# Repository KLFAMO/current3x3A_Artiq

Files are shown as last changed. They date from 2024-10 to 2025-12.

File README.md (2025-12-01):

# current3x3A_Artiq
3 channel current driver (up to 3A each channel) compatible with Artiq

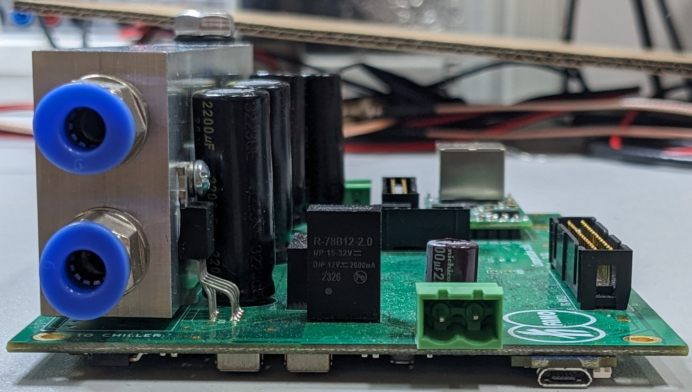
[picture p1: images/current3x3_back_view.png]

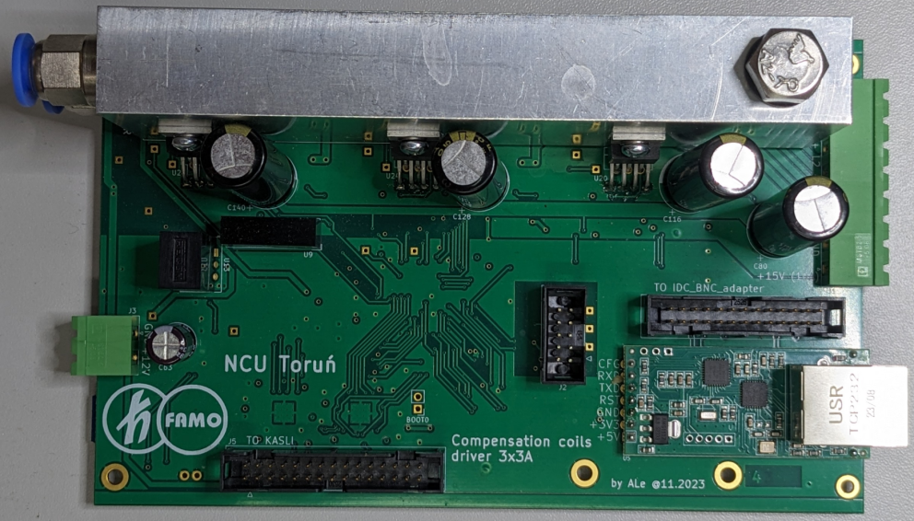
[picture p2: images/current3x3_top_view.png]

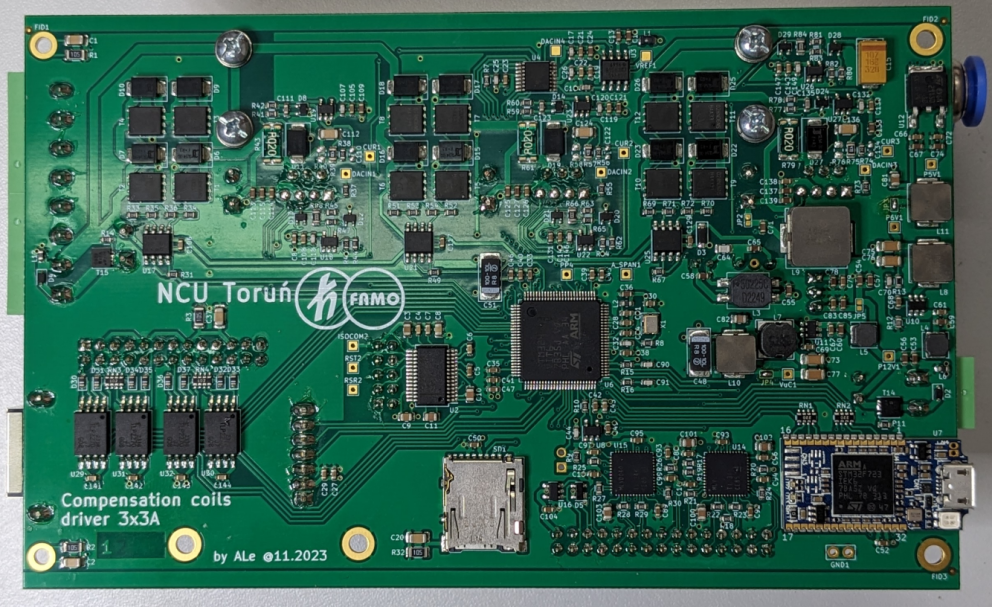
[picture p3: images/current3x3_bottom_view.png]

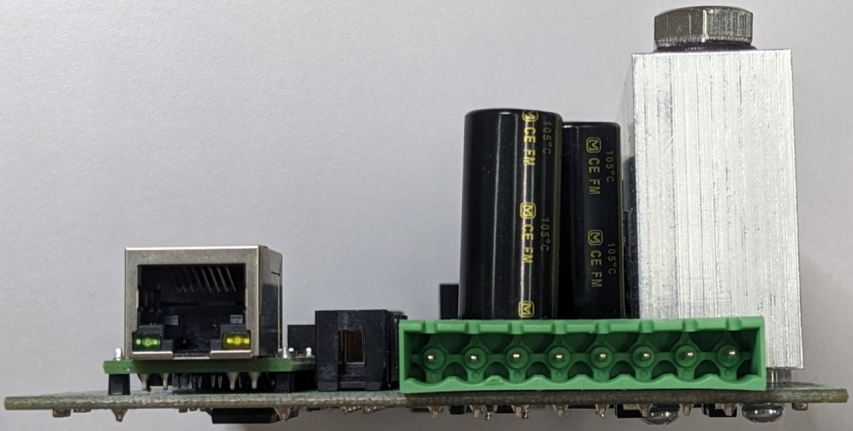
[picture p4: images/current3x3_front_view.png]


# Ports

Main power supply (- and +) 10A, 15V.

3x compensating coils.

Power supply for low power control circuits (optional). This power supplay can be taken from the main power supply (using jumpers).

Ethernet - user interface.

Water cooling.

# Input configuration

`TTL0` - triger, rising edge triggers current state

`TTL1`, `TTL2`, `TTL3` - determines current state TTL1 is the least significant bit.   
(`TTL1`=0, `TTL2`=0, `TTL3`=0) -> `state 0`  
(`TTL1`=1, `TTL2`=0, `TTL3`=0) -> `state 1`  
(`TTL1`=0, `TTL2`=1, `TTL3`=0) -> `state 2`  
...  
(`TTL1`=1, `TTL2`=1, `TTL3`=1) -> `state 7`

TTLs inputs are configurated in pull-down mode.

# User Interface

The user interface is available via TCP/IP. TCP232 module is used for Ethernet TCP/IP communication. IP address is configurable on http server. After connecting to the device, the user can change settings by sending commands.

## Setting Ethernet
- type IP address in web browser (default-from factory TCP232 module IP is 192.168.0.7)
- switch to `Serial Port` tab and set `Work Mode` to `TCP Server` and `Local Port Number` which will be used to connect to device
- IP configuration may be changed in `Local IP Config` tab.

## Connecting to the device

Example in nc. In Windows you may need to switch to bash.
```
nc 192.168.3.96 10
```

## Commands

There are 8 ttl states available, s0 (ttl=000), s1 (ttl=001), ..., s7 (ttl=111).

For each state, there are parameters: v1 (current in 1st coil), v2 (current in 2nd coil), v3 (current in 3th coil), t (time in ms of ramp before reaching these values). Current can be set between -3A to 3A. Minimum time t is 1ms.

Example:

`S1:V2 1.3` - set current 1.3A in 2nd coil for ttl state 001

`S0:V3 -0.23` - set current -0.23A in 3th coil for ttl state 000

`S2:T 5` - set time of ramp to 5 ms

`S1:V1 ?` - display value of 1st coil for state 001

`STATE ?` - display current ttl state 

Commands can be joined using `;` separator: ex. `s1:v2 2.1; s1:t 3` (max 100 characters in one message)

---

# Flashing Firmware to STM32 with ST-LINK

The firmware file to upload is located here: firmware/current3x3A_Artiq.hex

## Using STM32CubeProgrammer (GUI)

1. Connect the STM32 board to your computer via **ST-LINK**.  
2. Open **STM32CubeProgrammer**.  
3. Select **ST-LINK** as the interface and click **Connect**.  
4. In **Erasing & Programming**:  
   - Select `firmware/current3x3A_Artiq.hex`.  
   - Enable **Verify programming** (recommended).  
   - Click **Start Programming**.  
5. The board will restart with the new firmware.  

---

## Using STM32CubeProgrammer (CLI)

```bash
STM32_Programmer_CLI -c port=SWD -w firmware/current3x3A_Artiq.hex -v -rst
```

# License

[MIT](https://opensource.org/licenses/MIT)

# Acknowledgments
This work has received funding from the European Partnership on Metrology, co-financed by the European Union’s Horizon Europe Research and Innovation Programme and by the Participating States, under grant number 22IEM01 TOCK.

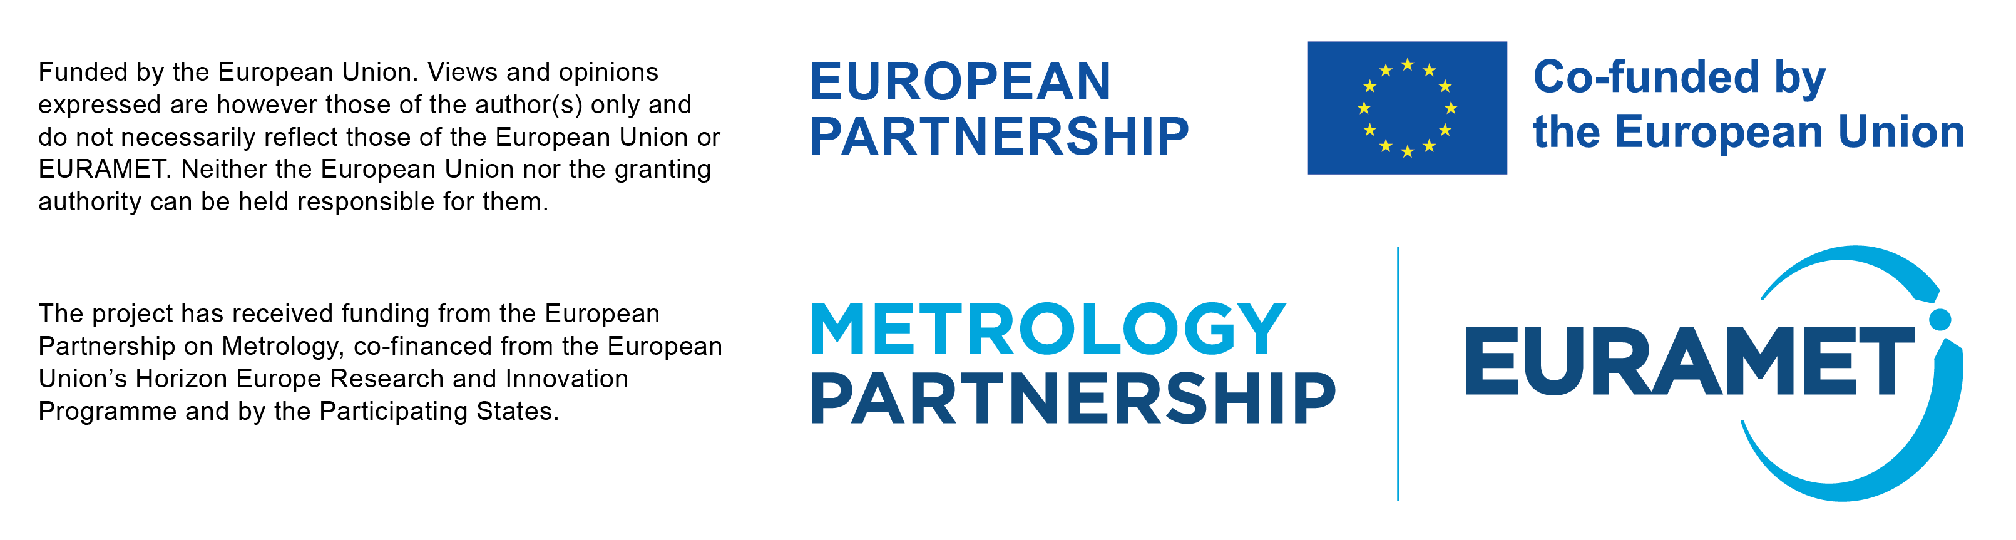
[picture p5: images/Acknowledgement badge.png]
badge


# Issues

Please add your comments in the `Issues` Github section (at the top of this page).

### Known issues
- communication issues when not nc in linux is used

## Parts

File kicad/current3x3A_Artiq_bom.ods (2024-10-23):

Source: | D:\Projekty\FAMO\current3x3A_Artiq\current3x3A_Artiq.kicad_sch
Date: | 13.11.2023 09:20:53
Tool: | Eeschema 7.0.1
Generator: | C:\Program Files\KiCad\bin\scripting\plugins/bom_csv_grouped_by_value.py
Component Count: | 353
Item | Qty | Reference(s) | Value | LibPart | Footprint | Datasheet | Comm
1 | 53 | C5, C14, C16, C21, C22, C23, C28, C29, C30, C34, C38, C39, C40, C41, C42, C49, C50, C52, C61, C62, C67, C68, C69, C72, C79, C83, C88, C89, C92, C93, C94, C95, C96, C97, C98, C99, C104, C105, C106, C108, C114, C117, C119, C126, C129, C130, C138, C141, C142, C143, C144, C145, C148 | 100n 50V X7R | Device:C | Capacitor_SMD:C_0603_1608Metric | ~
2 | 9 | C17, C26, C70, C107, C118, C120, C132, C146, C149 | 100p 50V C0G | Device:C | Capacitor_SMD:C_0603_1608Metric | ~
3 | 25 | C12, C24, C36, C53, C54, C55, C56, C57, C58, C59, C60, C65, C66, C71, C74, C78, C85, C109, C113, C115, C121, C125, C127, C133, C137, C139 | 10u 25V X5R | Device:C | Capacitor_SMD:C_0603_1608Metric | ~ | GRM188R61E106KA73D
4 | 3 | C25, C32, C44 | 15p 50V C0G | Device:C | Capacitor_SMD:C_0603_1608Metric | ~
5 | 4 | C18, C111, C123, C135 | 1n 50V C0G | Device:C | Capacitor_SMD:C_0603_1608Metric | ~
6 | 2 | C33, C35 | 2u2 10V X7R | Device:C | Capacitor_SMD:C_0603_1608Metric | ~
7 | 3 | C4, C6, C7 | 470n 25V X7R | Device:C | Capacitor_SMD:C_0603_1608Metric | ~
8 | 3 | C27, C43, C47 | 4u7 10V X5R | Device:C | Capacitor_SMD:C_0603_1608Metric | ~
9 | 2 | C90, C91 | 82p 50V C0G | Device:C | Capacitor_SMD:C_0603_1608Metric | ~
10 | 0 | C110, C122, C134 | DNP | Device:C | Capacitor_SMD:C_0603_1608Metric | ~
11 | 8 | C13, C19, C31, C45, C46, C87, C131, C147 | GCM188R71E105KA64J | Device:C | Capacitor_SMD:C_0603_1608Metric | ~ | 1uF 25V X7R
12 | 1 | C8 | 10n 100V X7R | Device:C | Capacitor_SMD:C_0805_2012Metric | ~
13 | 1 | C64 | 1n 100V C0G | Device:C | Capacitor_SMD:C_0805_2012Metric | ~
14 | 2 | C3, C9 | 2,2u 25V X7R | Device:C | Capacitor_SMD:C_0805_2012Metric | ~
15 | 2 | C10, C11 | 470n 100V X7R | Device:C | Capacitor_SMD:C_0805_2012Metric | ~
16 | 6 | C81, C82, C100, C101, C102, C103 | GRM21BR71A106KA73L | Device:C | Capacitor_SMD:C_0805_2012Metric | ~ | 10u 10V X7R
17 | 3 | C112, C124, C136 | 100n 50V C0G | Device:C | Capacitor_SMD:C_1206_3216Metric | ~
18 | 4 | C1, C2, C20, C37 | GCJ31BR73A102KXJ1L | Device:C | Capacitor_SMD:C_1206_3216Metric | ~
19 | 4 | C73, C75, C76, C77 | GRM31CR71A226KE15L | Device:C | Capacitor_SMD:C_1206_3216Metric | ~ | 22u 10V X7R Murata
20 | 2 | C48, C51 | 293D107X9010C2TE3 | nucleo_H743-rescue:CP-Device | Capacitor_Tantalum_SMD:CP_EIA-7132-28_AVX-C |  | 100u 6,3V tantal case C
21 | 1 | C15 | 100u 16V | c3Av2_A-rescue:CP-Device | Capacitor_Tantalum_SMD:CP_EIA-7343-31_Kemet-D |  | tantal, case D
22 | 4 | C80, C116, C128, C140 | 2200u 25V | c3Av2_A-rescue:CP-Device | Capacitor_THT:CP_Radial_D12.5mm_P5.00mm |  | 5000h Ø12,5 P5,0mm 105°C
23 | 1 | C63 | 100u 25V | c100AvA-rescue:CP-Device | Capacitor_THT:CP_Radial_D8.0mm_P3.50mm |  | >=5000h, 105°C, Ø8x11,5mm, P3,5mm
24 | 1 | SD1 | DM3AT-SF-PEJM5 | c3Av2_A-rescue:Micro_SD_Card_Det-Connector | Connector_Card:microSD_HC_Hirose_DM3AT-SF-PEJM5 | https://www.hirose.com/product/document?clcode=CL0609-0033-6-00&productname=DM3AT-SF-PEJ2M5&series=DM3&documenttype=Catalog&lang=en&documentid=D49662_en
25 | 1 | J2 | N2510-6002-RB | Connector_Generic:Conn_02x05_Odd_Even | Connector_IDC:IDC-Header_2x05_P2.54mm_Vertical | ~
26 | 1 | J6 | N2526-6002RB | Connector:Conn_01x26_Pin | Connector_IDC:IDC-Header_2x13_P2.54mm_Vertical | ~
27 | 1 | J5 | N2530-6002-RB | Connector_Generic:Conn_02x15_Odd_Even | Connector_IDC:IDC-Header_2x15_P2.54mm_Vertical | ~
28 | 1 | J3 | MSTBA2.5/2-G-5.08 1757242 | Connector_Generic:Conn_01x02 | Connector_Phoenix_MSTB:PhoenixContact_MSTBA_2,5_2-G-5,08_1x02_P5.08mm_Horizontal | ~
29 | 1 | J1 | MSTBA2.5/8-G-5.08 1757307 | Connector:Conn_01x08_Pin | Connector_Phoenix_MSTB:PhoenixContact_MSTBA_2,5_8-G-5,08_1x08_P5.08mm_Horizontal | ~
30 | 0 | BOOT0 | DNP | Connector_Generic:Conn_01x02 | Connector_PinHeader_2.54mm:PinHeader_1x02_P2.54mm_Vertical | ~ | igły 2x1x2,54
31 | 1 | U9 | AM2D-1218SZ | Regulator_Switching:NMA0505SC | Converter_DCDC:Converter_DCDC_Murata_NMAxxxxSC_THT | https://www.aimtec.com/site/Aimtec/files/Datasheet/HighResolution/AM2D-Z.pdf
32 | 1 | U13 | R-78B12-2.0 | Regulator_Switching:R-78B12-2.0 | Converter_DCDC:Converter_DCDC_RECOM_R-78B-2.0_THT | https://www.recom-power.com/pdf/Innoline/R-78Bxx-2.0.pdf
33 | 8 | D30, D31, D32, D33, D34, D35, D36, D37 | TS4148C RZG | Device:D_Filled | Diode_SMD:D_0603_1608Metric | ~
34 | 15 | D6, D7, D9, D10, D11, D15, D16, D17, D18, D19, D22, D23, D25, D26, D27 | SL54-3G | Device:D_Schottky | Diode_SMD:D_SMB | ~ | Diotec SL54-3G
35 | 1 | D3 | BZT52C20 | c3Av2_A-rescue:D_Zener_ALT-Device | Diode_SMD:D_SOD-123
36 | 1 | D2 | SD12C-01FTG | Diode:SD12_SOD323 | Diode_SMD:D_SOD-323 | https://www.littelfuse.com/~/media/electronics/datasheets/tvs_diode_arrays/littelfuse_tvs_diode_array_sd_c_datasheet.pdf.pdf
37 | 1 | D4 | SD15C-01FTG |  | Diode_SMD:D_SOD-323 | https://www.littelfuse.com/~/media/electronics/datasheets/tvs_diode_arrays/littelfuse_tvs_diode_array_sd_c_datasheet.pdf.pdf
38 | 2 | T14, T15 | SISS27DN-T1-GE3 | Transistor_FET:DMP3013SFV | ff_lib_7:Diodes_PowerDI3333-8 | https://www.diodes.com/assets/Datasheets/DMP3007SFG.pdf | SISA01DN-T1-GE3
39 | 4 | JP2, JP3, JP4, JP5 | Jumper_NO_Small | powersc7-rescue:Jumper_NO_Small-Device | ff_lib_7:GS2_small
40 | 1 | HS1 | Chłodnica miedziana by Janusz | Mechanical:Heatsink_Pad | ff_lib_7:Heatsink_cooler_20x140x40mm | ~ | Mount with: M3X10/D7985-A2 - 2pcs, K3.2/D125-A2 - 2pcs, K3/D127-A2 - 2 pcs, Bossard 1405322 - 4pcs.
41 | 7 | HS1 | M3X10/D7985-A2
42 | 7 | HS1 | K3.2/D125-A2
43 | 7 | HS1 | K3/D127-A2
44 | 4 | HS1 | Bossard 1405322
45 | 1 | L3 | 50225C Murata | c100AvA-rescue:L_Core_Ferrite_Coupled_1423-Device | ff_lib_7:L_CommonMode_Murata_5000 | https://www.murata-ps.com/pub/data/magnetics/kmp_5000c.pdf | or 50475C
46 | 2 | L4, L5 | LQH44PH220MPRL | powersc7-rescue:L_Core_Ferrite-Device | ff_lib_7:L_MURATA_LQH44 |  | 22u >0,5A 4x4mm
47 | 1 | X1 | ASE-8.000MHZ-L-C-T | Oscillator:ASE-xxxMHz | ff_lib_7:Oscillator_SMD_Abracon_ASE-4Pin_3.2x2.5mm | http://www.abracon.com/Oscillators/ASV.pdf
48 | 17 | R7, R8, R10, R17, R18, R19, R20, R21, R22, R23, R24, R25, R26, R27, R28, R29, R30 | 100R 1% | Device:R | Resistor_SMD:R_0603_1608Metric | ~
49 | 14 | R11, R14, R37, R38, R46, R47, R55, R56, R64, R65, R73, R74, R82, R83 | 10k 1% | Device:R | Resistor_SMD:R_0603_1608Metric | ~
50 | 6 | R41, R42, R59, R60, R77, R78 | 10R 1% | Device:R | Resistor_SMD:R_0603_1608Metric | ~
51 | 1 | R13 | 196k 1% | Device:R | Resistor_SMD:R_0603_1608Metric | ~
52 | 16 | R9, R31, R33, R34, R35, R36, R49, R51, R52, R53, R54, R67, R69, R70, R71, R72 | 1k 1% | Device:R | Resistor_SMD:R_0603_1608Metric | ~
53 | 2 | R15, R16 | 220R 1% | Device:R | Resistor_SMD:R_0603_1608Metric | ~
54 | 6 | R44, R45, R62, R63, R80, R81 | 24,9k 1% | Device:R | Resistor_SMD:R_0603_1608Metric | ~
55 | 1 | R12 | 30k 1% | Device:R | Resistor_SMD:R_0603_1608Metric | ~
56 | 1 | U7 | STLINK-V3MODS | ff:STLINK-V3MODS | ff_lib_7:STLINK-V3MODS | https://www.st.com/content/ccc/resource/technical/document/user_manual/group1/00/14/17/68/0f/01/48/01/DM00555046/files/DM00555046.pdf/jcr:content/translations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
57 | 1 | U5 | USR-TCP232-T2 | ff:USR-TCP232-T2 | ff_lib_7:USR-TC232-T2
58 | 2 | U14, U15 | SN65MLVD040RGZT | ff:SN65MLVD040 | ff_lib_7:VQFN-48-1EP_7x7mm_P0.5mm_EP4.1x4.1mm_ThermalVias | https://www.ti.com/lit/ds/symlink/sn65mlvd040.pdf
59 | 2 | L6, L12 | BLM18KG331SN1D | c100AvA-rescue:L_Core_Ferrite-Device | Inductor_SMD:L_0603_1608Metric |  | Murata
60 | 1 | L2 | LQM18DN330M70L | Device:L | Inductor_SMD:L_0603_1608Metric | ~ | LQM18DZ330M70L
61 | 1 | L1 | 33uH 200mA | Device:L | Inductor_SMD:L_0805_2012Metric | ~ | Viking NL05JTC330
62 | 1 | L7 | SRN6045-3R3Y | powersc7-rescue:L_Core_Ferrite-Device | Inductor_SMD:L_Bourns-SRN6028 |  | 3,3u >3A 6x6mm
63 | 1 | L8 | IHLP2525CZER100M01 | powersc7-rescue:L_Core_Ferrite-Device | Inductor_SMD:L_Vishay_IHLP-2525 |  | 10u >3A 6,5x6,5mm
64 | 2 | L10, L11 | IHLP2525CZER220M11 | powersc7-rescue:L_Core_Ferrite-Device | Inductor_SMD:L_Vishay_IHLP-2525 | https://www.vishay.com/docs/34104/ihlp-2525cz-01.pdf
65 | 1 | L9 | IHLP4040DZER100M11 | powersc7-rescue:L_Core_Ferrite-Device | Inductor_SMD:L_Vishay_IHLP-4040 |  | 10u >2A
66 | 1 | U6 | STM32H743VITx | MCU_ST_STM32H7:STM32H743VITx | Package_QFP:LQFP-100_14x14mm_P0.5mm | https://www.st.com/resource/en/datasheet/stm32h743vi.pdf
67 | 3 | U17, U21, U25 | IRS4428STRPBF | Driver_FET:MIC4428 | Package_SO:SO-8_3.9x4.9mm_P1.27mm | https://www.ixysic.com/home/pdfs.nsf/www/IX4426-27-28.pdf/$file/IX4426-27-28.pdf | MIC4428ZM
68 | 1 | U3 | ADR443BRZ | Reference_Voltage:ADR423ARMZ | Package_SO:SOIC-8_3.9x4.9mm_P1.27mm | https://www.analog.com/media/en/technical-documentation/data-sheets/ADR440_441_443_444_445.pdf
69 | 4 | U29, U30, U31, U32 | TLP2270(TP4,E | Isolator:HCPL-063A | Package_SO:SOIC-8_7.5x5.85mm_P1.27mm | http://docs.avagotech.com/docs/AV02-0391EN
70 | 1 | U2 | MAX3250CAI+ | ff:MAX3250CAI | Package_SO:SSOP-28_5.3x10.2mm_P0.65mm | https://datasheets.maximintegrated.com/en/ds/MAX3250.pdf | MAX3250EAI+
71 | 1 | U4 | DAC8555IPW | ff:DAC8555IPW | Package_SO:TSSOP-16_4.4x5mm_P0.65mm | http://www.ti.com/lit/gpn/dac8555
72 | 1 | D5 | WE 8240136 | Power_Protection:PRTR5V0U2X | Package_TO_SOT_SMD:SOT-143 | https://assets.nexperia.com/documents/data-sheet/PRTR5V0U2X.pdf | PRTR5V0U2X
73 | 2 | U8, U16 | 24AA02E48T-I/OT | Memory_EEPROM:24AA02-OT | Package_TO_SOT_SMD:SOT-23-5 | https://ww1.microchip.com/downloads/en/DeviceDoc/24AA02E48-24AA025E48-24AA02E64-24AA025E64-Data-Sheet-20002124H.pdf
74 | 3 | U19, U23, U27 | INA293B2IDBV | Amplifier_Current:INA196 | Package_TO_SOT_SMD:SOT-23-5 | https://www.ti.com/lit/ds/symlink/ina293.pdf?ts=1623847588072
75 | 3 | U18, U22, U26 | OPA191IDBVx | Amplifier_Operational:OPA196xDBV | Package_TO_SOT_SMD:SOT-23-5 | http://www.ti.com/lit/ds/symlink/opa4196.pdf | OPA196IDBVx
76 | 3 | D12, D20, D28 | BAT54CW | Diode:BAT54C | Package_TO_SOT_SMD:SOT-323_SC-70 | http://www.diodes.com/_files/datasheets/ds11005.pdf
77 | 3 | D13, D21, D29 | BAT54SW | Diode:BAT54SW | Package_TO_SOT_SMD:SOT-323_SC-70 | https://assets.nexperia.com/documents/data-sheet/BAT54W_SER.pdf
78 | 3 | D8, D14, D24 | BZB784-C15,115 | c3Av2_A-rescue:D_Zener_x2_ACom_KKA-Device | Package_TO_SOT_SMD:SOT-323_SC-70
79 | 12 | T1, T2, T3, T4, T5, T6, T7, T8, T9, T10, T11, T12 | BSC028N06NSATMA1 | Transistor_FET:BSC028N06LS3 | Package_TO_SOT_SMD:TDSON-8-1 | http://www.infineon.com/dgdl/Infineon-BSC028N06LS3-DS-v02_02-en.pdf?fileId=db3a30431ddc9372011ebafa4c607f8c
80 | 1 | U12 | LD29150DT50R | current100A-rescue:L7805-Regulator_Linear | Package_TO_SOT_SMD:TO-252-2 | https://www.st.com/content/ccc/resource/technical/document/datasheet/cc/41/70/73/f5/e6/40/50/CD00003403.pdf/files/CD00003403.pdf/jcr:content/translations/en.C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
81 | 1 | U10 | AP63200WU-7 | Regulator_Switching:AP63200WU | Package_TO_SOT_SMD:TSOT-23-6 | https://www.diodes.com/assets/Datasheets/AP63200-AP63201-AP63203-AP63205.pdf
82 | 1 | U11 | AP63203WU-7 | Regulator_Switching:AP63205WU | Package_TO_SOT_SMD:TSOT-23-6 | https://www.diodes.com/assets/Datasheets/AP63200-AP63201-AP63203-AP63205.pdf
83 | 3 | U20, U24, U28 | OPA548T | ff:OPA548T | Package_TO_SOT_THT:TO-220-7_P2.54x3.7mm_StaggerOdd_Lead3.8mm_Vertical | https://www.ti.com/lit/ds/symlink/opa548.pdf | OPA548T1
84 | 3 | R48, R66, R84 | 100R | Device:R | Resistor_SMD:R_0805_2012Metric | ~
85 | 3 | R39, R57, R75 | 47R | Device:R | Resistor_SMD:R_0805_2012Metric | ~
86 | 0 | R40, R58, R76 | DNP | Device:R | Resistor_SMD:R_0805_2012Metric | ~
87 | 4 | R1, R2, R3, R32 | HV732BTTD1004F | Device:R | Resistor_SMD:R_1206_3216Metric | ~
88 | 3 | R43, R61, R79 | 0R02 0,5% 1W 50ppm | Device:R | Resistor_SMD:R_2512_6332Metric | ~ | LVK24R020DER
89 | 2 | RN3, RN4 | CAT16-102J4LF | Device:R_Pack04 | Resistor_SMD:R_Array_Concave_4x0603 | ~
90 | 2 | RN1, RN2 | CAT16-220J4LF | Device:R_Pack04 | Resistor_SMD:R_Array_Concave_4x0603 | ~

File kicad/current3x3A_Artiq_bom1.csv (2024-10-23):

Source: | D:\Projekty\FAMO\current3x3A_Artiq\current3x3A_Artiq.kicad_sch
Date: | 13.11.2023 09:20:53
Tool: | Eeschema 7.0.1
Generator: | C:\Program Files\KiCad\bin\scripting\plugins/bom_csv_grouped_by_value.py
Component Count: | 363
Individual Components:
Item | Qty | Reference(s) | Value | LibPart | Footprint | Datasheet | Comm | Manufacturer_Name | Manufacturer_Part_Number | Mouser Part Number | Mouser Price/Stock | Sim.Device | Sim.Pins
 |  | A_SPAN1 | PAD | Connector:TestPoint | TestPoint:TestPoint_THTPad_1.5x1.5mm_Drill0.7mm | ~
 |  | BOOT1 | igły 2x1x2,54 | Connector_Generic:Conn_01x02 | Connector_PinHeader_2.54mm:PinHeader_1x02_P2.54mm_Vertical | ~
 |  | C1 | GCJ31BR73A102KXJ1L | Device:C | Capacitor_SMD:C_1206_3216Metric | ~
 |  | C2 | GCJ31BR73A102KXJ1L | Device:C | Capacitor_SMD:C_1206_3216Metric | ~
 |  | C3 | 2,2u 25V X7R | Device:C | Capacitor_SMD:C_0805_2012Metric | ~
 |  | C4 | 470n 25V X7R | Device:C | Capacitor_SMD:C_0603_1608Metric | ~
 |  | C5 | 100n 50V X7R | Device:C | Capacitor_SMD:C_0603_1608Metric | ~
 |  | C6 | 470n 25V X7R | Device:C | Capacitor_SMD:C_0603_1608Metric | ~
 |  | C7 | 470n 25V X7R | Device:C | Capacitor_SMD:C_0603_1608Metric | ~
 |  | C8 | 10n 100V X7R | Device:C | Capacitor_SMD:C_0805_2012Metric | ~
 |  | C9 | 2,2u 25V X7R | Device:C | Capacitor_SMD:C_0805_2012Metric | ~
 |  | C10 | 470n 100V X7R | Device:C | Capacitor_SMD:C_0805_2012Metric | ~
 |  | C11 | 470n 100V X7R | Device:C | Capacitor_SMD:C_0805_2012Metric | ~
 |  | C12 | 10u 25V X5R | Device:C | Capacitor_SMD:C_0603_1608Metric | ~ | GRM188R61E106KA73D
 |  | C13 | 1u 25V X7R | Device:C | Capacitor_SMD:C_0603_1608Metric | ~
 |  | C14 | 100n 50V X7R | Device:C | Capacitor_SMD:C_0603_1608Metric | ~
 |  | C15 | 100u 16V | c3Av2_A-rescue:CP-Device | Capacitor_Tantalum_SMD:CP_EIA-7343-31_Kemet-D |  | tantal, case D
 |  | C16 | 100n 50V X7R | Device:C | Capacitor_SMD:C_0603_1608Metric | ~
 |  | C17 | 100p 50V C0G | Device:C | Capacitor_SMD:C_0603_1608Metric | ~
 |  | C18 | 1n 50V C0G | Device:C | Capacitor_SMD:C_0603_1608Metric | ~
 |  | C19 | 1u 25V X7R | Device:C | Capacitor_SMD:C_0603_1608Metric | ~
 |  | C20 | GCJ31BR73A102KXJ1L | Device:C | Capacitor_SMD:C_1206_3216Metric | ~
 |  | C21 | 100n 50V X7R | Device:C | Capacitor_SMD:C_0603_1608Metric | ~
 |  | C22 | 100n 50V X7R | Device:C | Capacitor_SMD:C_0603_1608Metric | ~
 |  | C23 | 100n 50V X7R | Device:C | Capacitor_SMD:C_0603_1608Metric | ~
 |  | C24 | 10u 25V X5R | Device:C | Capacitor_SMD:C_0603_1608Metric | ~ | GRM188R61E106KA73D
 |  | C25 | 15p 50V C0G | Device:C | Capacitor_SMD:C_0603_1608Metric | ~
 |  | C26 | 100p 50V C0G | Device:C | Capacitor_SMD:C_0603_1608Metric | ~
 |  | C27 | 4u7 10V X5R | Device:C | Capacitor_SMD:C_0603_1608Metric | ~
 |  | C28 | 100n 50V X7R | Device:C | Capacitor_SMD:C_0603_1608Metric | ~
 |  | C29 | 100n 50V X7R | Device:C | Capacitor_SMD:C_0603_1608Metric | ~
 |  | C30 | 100n 50V X7R | Device:C | Capacitor_SMD:C_0603_1608Metric | ~
 |  | C31 | GCM188R71E105KA64J | Device:C | Capacitor_SMD:C_0603_1608Metric | ~ | 1uF 25V X7R
 |  | C32 | 15p 50V C0G | Device:C | Capacitor_SMD:C_0603_1608Metric | ~
 |  | C33 | 2u2 10V X7R | Device:C | Capacitor_SMD:C_0603_1608Metric | ~
 |  | C34 | 100n 50V X7R | Device:C | Capacitor_SMD:C_0603_1608Metric | ~
 |  | C35 | 2u2 10V X7R | Device:C | Capacitor_SMD:C_0603_1608Metric | ~
 |  | C36 | GRM21BR61E106KA73L | Device:C | Capacitor_SMD:C_0603_1608Metric | ~ | 10u X5R 25V
 |  | C37 | GCJ31BR73A102KXJ1L | Device:C | Capacitor_SMD:C_1206_3216Metric | ~
 |  | C38 | 100n 50V X7R | Device:C | Capacitor_SMD:C_0603_1608Metric | ~
 |  | C39 | 100n 50V X7R | Device:C | Capacitor_SMD:C_0603_1608Metric | ~
 |  | C40 | 100n 50V X7R | Device:C | Capacitor_SMD:C_0603_1608Metric | ~
 |  | C41 | 100n 50V X7R | Device:C | Capacitor_SMD:C_0603_1608Metric | ~
 |  | C42 | 100n 50V X7R | Device:C | Capacitor_SMD:C_0603_1608Metric | ~
 |  | C43 | 4u7 10V X5R | Device:C | Capacitor_SMD:C_0603_1608Metric | ~
 |  | C44 | 15p 50V C0G | Device:C | Capacitor_SMD:C_0603_1608Metric | ~
 |  | C45 | GCM188R71E105KA64J | Device:C | Capacitor_SMD:C_0603_1608Metric | ~ | 1uF 25V X7R
 |  | C46 | GCM188R71E105KA64J | Device:C | Capacitor_SMD:C_0603_1608Metric | ~ | 1uF 25V X7R
 |  | C47 | 4u7 10V X5R | Device:C | Capacitor_SMD:C_0603_1608Metric | ~
 |  | C48 | 293D107X9010C2TE3 | nucleo_H743-rescue:CP-Device | Capacitor_Tantalum_SMD:CP_EIA-7132-28_AVX-C |  | 100u 6,3V tantal case C
 |  | C49 | 100n 50V X7R | Device:C | Capacitor_SMD:C_0603_1608Metric | ~
 |  | C50 | 100n 50V X7R | Device:C | Capacitor_SMD:C_0603_1608Metric | ~
 |  | C51 | 293D107X9010C2TE3 | nucleo_H743-rescue:CP-Device | Capacitor_Tantalum_SMD:CP_EIA-7132-28_AVX-C |  | 100u 6,3V tantal case C
 |  | C52 | 100n 50V X7R | Device:C | Capacitor_SMD:C_0603_1608Metric | ~
 |  | C53 | 10u 25V X5R | Device:C | Capacitor_SMD:C_0603_1608Metric | ~ | GRM188R61E106KA73D
 |  | C54 | 10u 25V X5R | Device:C | Capacitor_SMD:C_0603_1608Metric | ~ | GRM188R61E106KA73D
 |  | C55 | 10u 25V X5R | Device:C | Capacitor_SMD:C_0603_1608Metric | ~ | GRM188R61E106KA73D
 |  | C56 | 10u 25V X5R | Device:C | Capacitor_SMD:C_0603_1608Metric | ~ | GRM188R61E106KA73D
 |  | C57 | 10u 25V X5R | Device:C | Capacitor_SMD:C_0603_1608Metric | ~ | GRM188R61E106KA73D
 |  | C58 | 10u 25V X5R | Device:C | Capacitor_SMD:C_0603_1608Metric | ~ | GRM188R61E106KA73D
 |  | C59 | 10u 25V X5R | Device:C | Capacitor_SMD:C_0603_1608Metric | ~ | GRM188R61E106KA73D
 |  | C60 | 10u 25V X5R | Device:C | Capacitor_SMD:C_0603_1608Metric | ~ | GRM188R61E106KA73D
 |  | C61 | 100n 50V X7R | Device:C | Capacitor_SMD:C_0603_1608Metric | ~
 |  | C62 | 100n 50V X7R | Device:C | Capacitor_SMD:C_0603_1608Metric | ~
 |  | C63 | 100u 25V | c100AvA-rescue:CP-Device | Capacitor_THT:CP_Radial_D8.0mm_P3.50mm |  | >=5000h, 105°C, Ø8x11,5mm, P3,5mm
 |  | C64 | 1n C0G 100V | Device:C | Capacitor_SMD:C_0805_2012Metric | ~
 |  | C65 | 10u 25V X5R | Device:C | Capacitor_SMD:C_0603_1608Metric | ~ | GRM188R61E106KA73D
 |  | C66 | 10u 25V X5R | Device:C | Capacitor_SMD:C_0603_1608Metric | ~ | GRM188R61E106KA73D
 |  | C67 | 100n 50V X7R | Device:C | Capacitor_SMD:C_0603_1608Metric | ~
 |  | C68 | 100n 50V X7R | Device:C | Capacitor_SMD:C_0603_1608Metric | ~
 |  | C69 | 100n 50V X7R | Device:C | Capacitor_SMD:C_0603_1608Metric | ~
 |  | C70 | 100p 50V C0G | Device:C | Capacitor_SMD:C_0603_1608Metric | ~
 |  | C71 | 10u 25V X5R | Device:C | Capacitor_SMD:C_0603_1608Metric | ~ | GRM188R61E106KA73D
 |  | C72 | 100n 50V X7R | Device:C | Capacitor_SMD:C_0603_1608Metric | ~
 |  | C73 | GRM31CR71A226KE15L | Device:C | Capacitor_SMD:C_1206_3216Metric | ~ | 22u 10V X7R Murata
 |  | C74 | 10u 25V X5R | Device:C | Capacitor_SMD:C_0603_1608Metric | ~ | GRM188R61E106KA73D
 |  | C75 | GRM31CR71A226KE15L | Device:C | Capacitor_SMD:C_1206_3216Metric | ~ | 22u 10V X7R Murata
 |  | C76 | GRM31CR71A226KE15L | Device:C | Capacitor_SMD:C_1206_3216Metric | ~ | 22u 10V X7R Murata
 |  | C77 | GRM31CR71A226KE15L | Device:C | Capacitor_SMD:C_1206_3216Metric | ~ | 22u 10V X7R Murata
 |  | C78 | 10u 25V X5R | Device:C | Capacitor_SMD:C_0603_1608Metric | ~ | GRM188R61E106KA73D
 |  | C79 | 100n 50V X7R | Device:C | Capacitor_SMD:C_0603_1608Metric | ~
 |  | C80 | 2200u 25V | c3Av2_A-rescue:CP-Device | Capacitor_THT:CP_Radial_D12.5mm_P5.00mm |  | 5000h Ø12,5 P5,0mm 105°C
 |  | C81 | GRM21BR71A106KA73L | Device:C | Capacitor_SMD:C_0805_2012Metric | ~ | 10u 10V X7R
 |  | C82 | GRM21BR71A106KA73L | Device:C | Capacitor_SMD:C_0805_2012Metric | ~ | 10u 10V X7R
 |  | C83 | 100n 50V X7R | Device:C | Capacitor_SMD:C_0603_1608Metric | ~
 |  | C85 | 10u 25V X5R | Device:C | Capacitor_SMD:C_0603_1608Metric | ~ | GRM188R61E106KA73D
 |  | C87 | GCM188R71E105KA64J | Device:C | Capacitor_SMD:C_0603_1608Metric | ~ | 1uF 25V X7R
 |  | C88 | 100n 50V X7R | Device:C | Capacitor_SMD:C_0603_1608Metric | ~
 |  | C89 | 100n 50V X7R | Device:C | Capacitor_SMD:C_0603_1608Metric | ~
 |  | C90 | 82p 50V C0G | Device:C | Capacitor_SMD:C_0603_1608Metric | ~
 |  | C91 | 82p 50V C0G | Device:C | Capacitor_SMD:C_0603_1608Metric | ~
 |  | C92 | 100n 50V X7R | Device:C | Capacitor_SMD:C_0603_1608Metric | ~
 |  | C93 | 100n 50V X7R | Device:C | Capacitor_SMD:C_0603_1608Metric | ~
 |  | C94 | 100n 50V X7R | Device:C | Capacitor_SMD:C_0603_1608Metric | ~
 |  | C95 | 100n 50V X7R | Device:C | Capacitor_SMD:C_0603_1608Metric | ~
 |  | C96 | 100n 50V X7R | Device:C | Capacitor_SMD:C_0603_1608Metric | ~
 |  | C97 | 100n 50V X7R | Device:C | Capacitor_SMD:C_0603_1608Metric | ~
 |  | C98 | 100n 50V X7R | Device:C | Capacitor_SMD:C_0603_1608Metric | ~
 |  | C99 | 100n 50V X7R | Device:C | Capacitor_SMD:C_0603_1608Metric | ~
 |  | C100 | GRM21BR71A106KA73L | Device:C | Capacitor_SMD:C_0805_2012Metric | ~ | 10u 10V X7R
 |  | C101 | GRM21BR71A106KA73L | Device:C | Capacitor_SMD:C_0805_2012Metric | ~ | 10u 10V X7R
 |  | C102 | GRM21BR71A106KA73L | Device:C | Capacitor_SMD:C_0805_2012Metric | ~ | 10u 10V X7R
 |  | C103 | GRM21BR71A106KA73L | Device:C | Capacitor_SMD:C_0805_2012Metric | ~ | 10u 10V X7R
 |  | C104 | 100n 50V X7R | Device:C | Capacitor_SMD:C_0603_1608Metric | ~
 |  | C105 | 100n 50V X7R | Device:C | Capacitor_SMD:C_0603_1608Metric | ~
 |  | C106 | 100n 50V X7R | Device:C | Capacitor_SMD:C_0603_1608Metric | ~
 |  | C107 | 100p 50V C0G | Device:C | Capacitor_SMD:C_0603_1608Metric | ~
 |  | C108 | 100n X7R 50V | Device:C | Capacitor_SMD:C_0603_1608Metric | ~
 |  | C109 | 10u 25V X5R | Device:C | Capacitor_SMD:C_0603_1608Metric | ~ | GRM188R61E106KA73D
 |  | C110 | DNP | Device:C | Capacitor_SMD:C_0603_1608Metric | ~
 |  | C111 | 1n 50V C0G | Device:C | Capacitor_SMD:C_0603_1608Metric | ~
 |  | C112 | 100n 50V C0G | Device:C | Capacitor_SMD:C_1206_3216Metric | ~
 |  | C113 | 10u 25V X5R | Device:C | Capacitor_SMD:C_0603_1608Metric | ~ | GRM188R61E106KA73D
 |  | C114 | 100n 50V X7R | Device:C | Capacitor_SMD:C_0603_1608Metric | ~
 |  | C115 | 10u 25V X5R | Device:C | Capacitor_SMD:C_0603_1608Metric | ~ | GRM188R61E106KA73D
 |  | C116 | 2200u 25V | c3Av2_A-rescue:CP-Device | Capacitor_THT:CP_Radial_D12.5mm_P5.00mm |  | 5000h Ø12,5 P5,0mm 105°C
 |  | C117 | 100n 50V X7R | Device:C | Capacitor_SMD:C_0603_1608Metric | ~
 |  | C118 | 100p C0G 50V | Device:C | Capacitor_SMD:C_0603_1608Metric | ~
 |  | C119 | 100n 50V X7R | Device:C | Capacitor_SMD:C_0603_1608Metric | ~
 |  | C120 | 100p 50V C0G | Device:C | Capacitor_SMD:C_0603_1608Metric | ~
 |  | C121 | 10u 25V X5R | Device:C | Capacitor_SMD:C_0603_1608Metric | ~ | GRM188R61E106KA73D
 |  | C122 | DNP | Device:C | Capacitor_SMD:C_0603_1608Metric | ~
 |  | C123 | 1n 50V C0G | Device:C | Capacitor_SMD:C_0603_1608Metric | ~
 |  | C124 | 100n 50V C0G | Device:C | Capacitor_SMD:C_1206_3216Metric | ~
 |  | C125 | 10u 25V X5R | Device:C | Capacitor_SMD:C_0603_1608Metric | ~ | GRM188R61E106KA73D
 |  | C126 | 100n 50V X7R | Device:C | Capacitor_SMD:C_0603_1608Metric | ~
 |  | C127 | 10u 25V X5R | Device:C | Capacitor_SMD:C_0603_1608Metric | ~ | GRM188R61E106KA73D
 |  | C128 | 2200u 25V | c3Av2_A-rescue:CP-Device | Capacitor_THT:CP_Radial_D12.5mm_P5.00mm |  | 5000h Ø12,5 P5,0mm 105°C
 |  | C129 | 100n 50V X7R | Device:C | Capacitor_SMD:C_0603_1608Metric | ~
 |  | C130 | 100n 50V X7R | Device:C | Capacitor_SMD:C_0603_1608Metric | ~
 |  | C131 | GCM188R71E105KA64J | Device:C | Capacitor_SMD:C_0603_1608Metric | ~ | 1uF 25V X7R
 |  | C132 | 100p 50V C0G | Device:C | Capacitor_SMD:C_0603_1608Metric | ~
 |  | C133 | 10u 25V X5R | Device:C | Capacitor_SMD:C_0603_1608Metric | ~ | GRM188R61E106KA73D
 |  | C134 | DNP | Device:C | Capacitor_SMD:C_0603_1608Metric | ~
 |  | C135 | 1n 50V C0G | Device:C | Capacitor_SMD:C_0603_1608Metric | ~
 |  | C136 | 100n 50V C0G | Device:C | Capacitor_SMD:C_1206_3216Metric | ~
 |  | C137 | 10u 25V X5R | Device:C | Capacitor_SMD:C_0603_1608Metric | ~ | GRM188R61E106KA73D
 |  | C138 | 100n 50V X7R | Device:C | Capacitor_SMD:C_0603_1608Metric | ~
 |  | C139 | 10u 25V X5R | Device:C | Capacitor_SMD:C_0603_1608Metric | ~ | GRM188R61E106KA73D
 |  | C140 | 2200u 25V | c3Av2_A-rescue:CP-Device | Capacitor_THT:CP_Radial_D12.5mm_P5.00mm |  | 5000h Ø12,5 P5,0mm 105°C
 |  | C141 | 100n 50V X7R | Device:C | Capacitor_SMD:C_0603_1608Metric | ~
 |  | C142 | 100n 50V X7R | Device:C | Capacitor_SMD:C_0603_1608Metric | ~
 |  | C143 | 100n 50V X7R | Device:C | Capacitor_SMD:C_0603_1608Metric | ~
 |  | C144 | 100n 50V X7R | Device:C | Capacitor_SMD:C_0603_1608Metric | ~
 |  | C145 | 100n X7R 50V | Device:C | Capacitor_SMD:C_0603_1608Metric | ~
 |  | C146 | 100p C0G 50V | Device:C | Capacitor_SMD:C_0603_1608Metric | ~
 |  | C147 | GCM188R71E105KA64J | Device:C | Capacitor_SMD:C_0603_1608Metric | ~ | 1uF 25V X7R
 |  | C148 | 100n X7R 50V | Device:C | Capacitor_SMD:C_0603_1608Metric | ~
 |  | C149 | 100p C0G 50V | Device:C | Capacitor_SMD:C_0603_1608Metric | ~
 |  | CUR1 | TestPoint | Connector:TestPoint | TestPoint:TestPoint_THTPad_1.5x1.5mm_Drill0.7mm | ~
 |  | CUR2 | TestPoint | Connector:TestPoint | TestPoint:TestPoint_THTPad_1.5x1.5mm_Drill0.7mm | ~
 |  | CUR3 | TestPoint | Connector:TestPoint | TestPoint:TestPoint_THTPad_1.5x1.5mm_Drill0.7mm | ~
 |  | D2 | SD12C-01FTG | Diode:SD12_SOD323 | Diode_SMD:D_SOD-323 | https://www.littelfuse.com/~/media/electronics/datasheets/tvs_diode_arrays/littelfuse_tvs_diode_array_sd_c_datasheet.pdf.pdf
 |  | D3 | BZT52C20 | c3Av2_A-rescue:D_Zener_ALT-Device | Diode_SMD:D_SOD-123
 |  | D4 | SD12C-01FTG | Diode:SD12_SOD323 | Diode_SMD:D_SOD-323 | https://www.littelfuse.com/~/media/electronics/datasheets/tvs_diode_arrays/littelfuse_tvs_diode_array_sd_c_datasheet.pdf.pdf
 |  | D5 | WE 8240136 | Power_Protection:PRTR5V0U2X | Package_TO_SOT_SMD:SOT-143 | https://assets.nexperia.com/documents/data-sheet/PRTR5V0U2X.pdf | PRTR5V0U2X
 |  | D6 | SL54-3G | Device:D_Schottky | Diode_SMD:D_SMB | ~ | Diotec SL54-3G
 |  | D7 | SL54-3G | Device:D_Schottky | Diode_SMD:D_SMB | ~ | Diotec SL54-3G
 |  | D8 | BZB784-C15,115 | c3Av2_A-rescue:D_Zener_x2_ACom_KKA-Device | Package_TO_SOT_SMD:SOT-323_SC-70
 |  | D9 | SL54-3G | Device:D_Schottky | Diode_SMD:D_SMB | ~ | Diotec SL54-3G
 |  | D10 | SL54-3G | Device:D_Schottky | Diode_SMD:D_SMB | ~ | Diotec SL54-3G
 |  | D11 | SL54-3G | Device:D_Schottky | Diode_SMD:D_SMB | ~ | Diotec SL54-3G
 |  | D12 | BAT54CW | Diode:BAT54C | Package_TO_SOT_SMD:SOT-323_SC-70 | http://www.diodes.com/_files/datasheets/ds11005.pdf
 |  | D13 | BAT54SW | Diode:BAT54SW | Package_TO_SOT_SMD:SOT-323_SC-70 | https://assets.nexperia.com/documents/data-sheet/BAT54W_SER.pdf
 |  | D14 | BZB784-C15,115 | c3Av2_A-rescue:D_Zener_x2_ACom_KKA-Device | Package_TO_SOT_SMD:SOT-323_SC-70
 |  | D15 | SL54-3G | Device:D_Schottky | Diode_SMD:D_SMB | ~ | Diotec SL54-3G
 |  | D16 | SL54-3G | Device:D_Schottky | Diode_SMD:D_SMB | ~ | Diotec SL54-3G
 |  | D17 | SL54-3G | Device:D_Schottky | Diode_SMD:D_SMB | ~ | Diotec SL54-3G
 |  | D18 | SL54-3G | Device:D_Schottky | Diode_SMD:D_SMB | ~ | Diotec SL54-3G
 |  | D19 | SL54-3G | Device:D_Schottky | Diode_SMD:D_SMB | ~ | Diotec SL54-3G
 |  | D20 | BAT54CW | Diode:BAT54C | Package_TO_SOT_SMD:SOT-323_SC-70 | http://www.diodes.com/_files/datasheets/ds11005.pdf
 |  | D21 | BAT54SW | Diode:BAT54SW | Package_TO_SOT_SMD:SOT-323_SC-70 | https://assets.nexperia.com/documents/data-sheet/BAT54W_SER.pdf
 |  | D22 | SL54-3G | Device:D_Schottky | Diode_SMD:D_SMB | ~ | Diotec SL54-3G
 |  | D23 | SL54-3G | Device:D_Schottky | Diode_SMD:D_SMB | ~ | Diotec SL54-3G
 |  | D24 | BZB784-C15,115 | c3Av2_A-rescue:D_Zener_x2_ACom_KKA-Device | Package_TO_SOT_SMD:SOT-323_SC-70
 |  | D25 | SL54-3G | Device:D_Schottky | Diode_SMD:D_SMB | ~ | Diotec SL54-3G
 |  | D26 | SL54-3G | Device:D_Schottky | Diode_SMD:D_SMB | ~ | Diotec SL54-3G
 |  | D27 | SL54-3G | Device:D_Schottky | Diode_SMD:D_SMB | ~ | Diotec SL54-3G
 |  | D28 | BAT54CW | Diode:BAT54C | Package_TO_SOT_SMD:SOT-323_SC-70 | http://www.diodes.com/_files/datasheets/ds11005.pdf
 |  | D29 | BAT54SW | Diode:BAT54SW | Package_TO_SOT_SMD:SOT-323_SC-70 | https://assets.nexperia.com/documents/data-sheet/BAT54W_SER.pdf
 |  | D30 | TS4148C RZG | Device:D_Filled | Diode_SMD:D_0603_1608Metric | ~ |  |  |  |  |  | D | 1=K 2=A
 |  | D31 | TS4148C RZG | Device:D_Filled | Diode_SMD:D_0603_1608Metric | ~ |  |  |  |  |  | D | 1=K 2=A
 |  | D32 | TS4148C RZG | Device:D_Filled | Diode_SMD:D_0603_1608Metric | ~ |  |  |  |  |  | D | 1=K 2=A
 |  | D33 | TS4148C RZG | Device:D_Filled | Diode_SMD:D_0603_1608Metric | ~ |  |  |  |  |  | D | 1=K 2=A
 |  | D34 | TS4148C RZG | Device:D_Filled | Diode_SMD:D_0603_1608Metric | ~ |  |  |  |  |  | D | 1=K 2=A
 |  | D35 | TS4148C RZG | Device:D_Filled | Diode_SMD:D_0603_1608Metric | ~ |  |  |  |  |  | D | 1=K 2=A
 |  | D36 | TS4148C RZG | Device:D_Filled | Diode_SMD:D_0603_1608Metric | ~ |  |  |  |  |  | D | 1=K 2=A
 |  | D37 | TS4148C RZG | Device:D_Filled | Diode_SMD:D_0603_1608Metric | ~ |  |  |  |  |  | D | 1=K 2=A
 |  | DACIN1 | TestPoint | Connector:TestPoint | TestPoint:TestPoint_THTPad_1.5x1.5mm_Drill0.7mm | ~
 |  | DACIN2 | TestPoint | Connector:TestPoint | TestPoint:TestPoint_THTPad_1.5x1.5mm_Drill0.7mm | ~
 |  | DACIN3 | TestPoint | Connector:TestPoint | TestPoint:TestPoint_THTPad_1.5x1.5mm_Drill0.7mm | ~
 |  | DACIN4 | TestPoint | Connector:TestPoint | TestPoint:TestPoint_Pad_1.5x1.5mm | ~
 |  | FID1 | Fiducial | Mechanical:Fiducial | Fiducial:Fiducial_0.5mm_Mask1.5mm | ~
 |  | FID2 | Fiducial | Mechanical:Fiducial | Fiducial:Fiducial_0.5mm_Mask1.5mm | ~
 |  | FID3 | Fiducial | Mechanical:Fiducial | Fiducial:Fiducial_0.5mm_Mask1.5mm | ~
 |  | GND1 | PAD | Connector:TestPoint | TestPoint:TestPoint_Bridge_Pitch2.54mm_Drill1.0mm | ~
 |  | H1 | MountingHole_Pad | Mechanical:MountingHole_Pad | MountingHole:MountingHole_2.7mm_M2.5_DIN965_Pad | ~
 |  | H2 | MountingHole_Pad | Mechanical:MountingHole_Pad | MountingHole:MountingHole_2.7mm_M2.5_DIN965_Pad | ~
 |  | H4 | MountingHole_Pad | Mechanical:MountingHole_Pad | MountingHole:MountingHole_3.2mm_M3_DIN965_Pad | ~
 |  | H6 | MountingHole_Pad | Mechanical:MountingHole_Pad | MountingHole:MountingHole_3.2mm_M3_DIN965_Pad | ~
 |  | H7 | MountingHole_Pad | Mechanical:MountingHole_Pad | MountingHole:MountingHole_3.2mm_M3_DIN965_Pad | ~
 |  | H8 | MountingHole_Pad | Mechanical:MountingHole_Pad | MountingHole:MountingHole_3.2mm_M3_DIN965_Pad | ~
 |  | HS1 | Chłodnica miedziana by Janusz | Mechanical:Heatsink_Pad | ff_lib_7:Heatsink_cooler_20x140x40mm | ~ | Mount with: M3X10/D7985-A2 - 2pcs, K3.2/D125-A2 - 2pcs, K3/D127-A2 - 2 pcs, Bossard 1405322 - 4pcs.
 |  | ISOCOM2 | TestPoint | Connector:TestPoint | TestPoint:TestPoint_THTPad_1.5x1.5mm_Drill0.7mm | ~
 |  | J1 | MSTBA2.5/8-G-5.08 1757307 | Connector:Conn_01x08_Pin | Connector_Phoenix_MSTB:PhoenixContact_MSTBA_2,5_8-G-5,08_1x08_P5.08mm_Horizontal | ~
 |  | J2 | N2510-6002-RB | Connector_Generic:Conn_02x05_Odd_Even | Connector_IDC:IDC-Header_2x05_P2.54mm_Vertical | ~
 |  | J3 | MSTBA2.5/2-G-5.08 1757242 | Connector_Generic:Conn_01x02 | Connector_Phoenix_MSTB:PhoenixContact_MSTBA_2,5_2-G-5,08_1x02_P5.08mm_Horizontal | ~
 |  | J5 | N2530-6002-RB | Connector_Generic:Conn_02x15_Odd_Even | Connector_IDC:IDC-Header_2x15_P2.54mm_Vertical | ~
 |  | J6 | N2526-6002RB | Connector:Conn_01x26_Pin | Connector_IDC:IDC-Header_2x13_P2.54mm_Vertical | ~
 |  | JP2 | Jumper_NO_Small | powersc7-rescue:Jumper_NO_Small-Device | ff_lib_7:GS2_small
 |  | JP3 | Jumper_NO_Small | powersc7-rescue:Jumper_NO_Small-Device | ff_lib_7:GS2_small
 |  | JP4 | Jumper_NO_Small | powersc7-rescue:Jumper_NO_Small-Device | ff_lib_7:GS2_small
 |  | JP5 | Jumper_NO_Small | powersc7-rescue:Jumper_NO_Small-Device | ff_lib_7:GS2_small
 |  | L1 | 33uH 200mA | Device:L | Inductor_SMD:L_0805_2012Metric | ~ | Viking NL05JTC330
 |  | L2 | LQM18DN330M70L | Device:L | Inductor_SMD:L_0603_1608Metric | ~ | LQM18DZ330M70L
 |  | L3 | 50225C Murata | c100AvA-rescue:L_Core_Ferrite_Coupled_1423-Device | ff_lib_7:L_CommonMode_Murata_5000 | https://www.murata-ps.com/pub/data/magnetics/kmp_5000c.pdf | or 50475C
 |  | L4 | LQH44PH220MPRL | powersc7-rescue:L_Core_Ferrite-Device | ff_lib_7:L_MURATA_LQH44 |  | 22u >0,5A 4x4mm
 |  | L5 | LQH44PH220MPRL | powersc7-rescue:L_Core_Ferrite-Device | ff_lib_7:L_MURATA_LQH44 |  | 22u >0,5A 4x4mm
 |  | L6 | BLM18KG331SN1D | c100AvA-rescue:L_Core_Ferrite-Device | Inductor_SMD:L_0603_1608Metric |  | Murata
 |  | L7 | SRN6045-3R3Y | powersc7-rescue:L_Core_Ferrite-Device | Inductor_SMD:L_Bourns-SRN6028 |  | 3,3u >3A 6x6mm
 |  | L8 | IHLP2525CZER100M01 | powersc7-rescue:L_Core_Ferrite-Device | Inductor_SMD:L_Vishay_IHLP-2525 |  | 10u >3A 6,5x6,5mm
 |  | L9 | IHLP4040DZER100M11 | powersc7-rescue:L_Core_Ferrite-Device | Inductor_SMD:L_Vishay_IHLP-4040 |  | 10u >2A
 |  | L10 | IHLP2525CZER220M11 | powersc7-rescue:L_Core_Ferrite-Device | Inductor_SMD:L_Vishay_IHLP-2525 | https://www.vishay.com/docs/34104/ihlp-2525cz-01.pdf
 |  | L11 | IHLP2525CZER220M11 | powersc7-rescue:L_Core_Ferrite-Device | Inductor_SMD:L_Vishay_IHLP-2525 | https://www.vishay.com/docs/34104/ihlp-2525cz-01.pdf
 |  | L12 | BLM18KG331SN1D | c100AvA-rescue:L_Core_Ferrite-Device | Inductor_SMD:L_0603_1608Metric |  | Murata
 |  | P5V1 | TestPoint | Connector:TestPoint | TestPoint:TestPoint_THTPad_1.5x1.5mm_Drill0.7mm | ~
 |  | P6V1 | TestPoint | Connector:TestPoint | TestPoint:TestPoint_THTPad_1.5x1.5mm_Drill0.7mm | ~
 |  | P12V1 | TestPoint | Connector:TestPoint | TestPoint:TestPoint_THTPad_1.5x1.5mm_Drill0.7mm | ~
 |  | PP4 | PAD | Connector:TestPoint | TestPoint:TestPoint_THTPad_1.5x1.5mm_Drill0.7mm | ~
 |  | R1 | HV732BTTD1004F | Device:R | Resistor_SMD:R_1206_3216Metric | ~
 |  | R2 | HV732BTTD1004F | Device:R | Resistor_SMD:R_1206_3216Metric | ~
 |  | R3 | HV732BTTD1004F | Device:R | Resistor_SMD:R_1206_3216Metric | ~
 |  | R7 | 100R 1% | Device:R | ff_lib_7:R_0603_ff | ~
 |  | R8 | 100R 1% | Device:R | ff_lib_7:R_0603_ff | ~
 |  | R9 | 1k 1% | Device:R | ff_lib_7:R_0603_ff | ~
 |  | R10 | 100R 1% | Device:R | ff_lib_7:R_0603_ff | ~
 |  | R11 | 10k 1% | Device:R | ff_lib_7:R_0603_ff | ~
 |  | R12 | 30k 1% | Device:R | ff_lib_7:R_0603_ff | ~
 |  | R13 | 196k 1% | Device:R | ff_lib_7:R_0603_ff | ~
 |  | R14 | 10k 1% | Device:R | ff_lib_7:R_0603_ff | ~
 |  | R15 | 220R 1% | Device:R | ff_lib_7:R_0603_ff | ~
 |  | R16 | 220R 1% | Device:R | ff_lib_7:R_0603_ff | ~
 |  | R17 | 100R 1% | Device:R | ff_lib_7:R_0603_ff | ~
 |  | R18 | 100R 1% | Device:R | ff_lib_7:R_0603_ff | ~
 |  | R19 | 100R 1% | Device:R | ff_lib_7:R_0603_ff | ~
 |  | R20 | 100R 1% | Device:R | ff_lib_7:R_0603_ff | ~
 |  | R21 | 100R 1% | Device:R | ff_lib_7:R_0603_ff | ~
 |  | R22 | 100R 1% | Device:R | ff_lib_7:R_0603_ff | ~
 |  | R23 | 100R 1% | Device:R | ff_lib_7:R_0603_ff | ~
 |  | R24 | 100R 1% | Device:R | ff_lib_7:R_0603_ff | ~
 |  | R25 | 100R 1% | Device:R | ff_lib_7:R_0603_ff | ~
 |  | R26 | 100R 1% | Device:R | ff_lib_7:R_0603_ff | ~
 |  | R27 | 100R 1% | Device:R | ff_lib_7:R_0603_ff | ~
 |  | R28 | 100R 1% | Device:R | ff_lib_7:R_0603_ff | ~
 |  | R29 | 100R 1% | Device:R | ff_lib_7:R_0603_ff | ~
 |  | R30 | 100R 1% | Device:R | ff_lib_7:R_0603_ff | ~
 |  | R31 | 1k 1% | Device:R | ff_lib_7:R_0603_ff | ~
 |  | R32 | HV732BTTD1004F | Device:R | Resistor_SMD:R_1206_3216Metric | ~
 |  | R33 | 1k 1% | Device:R | ff_lib_7:R_0603_ff | ~
 |  | R34 | 1k 1% | Device:R | ff_lib_7:R_0603_ff | ~
 |  | R35 | 1k 1% | Device:R | ff_lib_7:R_0603_ff | ~
 |  | R36 | 1k 1% | Device:R | ff_lib_7:R_0603_ff | ~
 |  | R37 | 10k 1% | Device:R | ff_lib_7:R_0603_ff | ~
 |  | R38 | 10k 1% | Device:R | ff_lib_7:R_0603_ff | ~
 |  | R39 | 47R | Device:R | Resistor_SMD:R_0805_2012Metric | ~
 |  | R40 | DNP | Device:R | Resistor_SMD:R_0805_2012Metric | ~
 |  | R41 | 10R | Device:R | ff_lib_7:R_0603_ff | ~
 |  | R42 | 10R | Device:R | ff_lib_7:R_0603_ff | ~
 |  | R43 | 0R02 0,5% 1W 50ppm | Device:R | Resistor_SMD:R_2512_6332Metric | ~ | LVK24R020DER
 |  | R44 | 24,9kk 1% | Device:R | ff_lib_7:R_0603_ff | ~
 |  | R45 | 24,9kk 1% | Device:R | ff_lib_7:R_0603_ff | ~
 |  | R46 | 10k 1% | Device:R | ff_lib_7:R_0603_ff | ~
 |  | R47 | 10k 1% | Device:R | ff_lib_7:R_0603_ff | ~
 |  | R48 | 100R | Device:R | Resistor_SMD:R_0805_2012Metric | ~
 |  | R49 | 1k 1% | Device:R | ff_lib_7:R_0603_ff | ~
 |  | R51 | 1k 1% | Device:R | ff_lib_7:R_0603_ff | ~
 |  | R52 | 1k 1% | Device:R | ff_lib_7:R_0603_ff | ~
 |  | R53 | 1k 1% | Device:R | ff_lib_7:R_0603_ff | ~
 |  | R54 | 1k 1% | Device:R | ff_lib_7:R_0603_ff | ~
 |  | R55 | 10k 1% | Device:R | ff_lib_7:R_0603_ff | ~
 |  | R56 | 10k 1% | Device:R | ff_lib_7:R_0603_ff | ~
 |  | R57 | 47R | Device:R | Resistor_SMD:R_0805_2012Metric | ~
 |  | R58 | DNP | Device:R | Resistor_SMD:R_0805_2012Metric | ~
 |  | R59 | 10R | Device:R | ff_lib_7:R_0603_ff | ~
 |  | R60 | 10R | Device:R | ff_lib_7:R_0603_ff | ~
 |  | R61 | 0R02 0,5% 1W 50ppm | Device:R | Resistor_SMD:R_2512_6332Metric | ~ | LVK24R020DER
 |  | R62 | 24,9kk 1% | Device:R | ff_lib_7:R_0603_ff | ~
 |  | R63 | 24,9kk 1% | Device:R | ff_lib_7:R_0603_ff | ~
 |  | R64 | 10k 1% | Device:R | ff_lib_7:R_0603_ff | ~
 |  | R65 | 10k 1% | Device:R | ff_lib_7:R_0603_ff | ~
 |  | R66 | 100R | Device:R | Resistor_SMD:R_0805_2012Metric | ~
 |  | R67 | 1k 1% | Device:R | ff_lib_7:R_0603_ff | ~
 |  | R69 | 1k 1% | Device:R | ff_lib_7:R_0603_ff | ~
 |  | R70 | 1k 1% | Device:R | ff_lib_7:R_0603_ff | ~
 |  | R71 | 1k 1% | Device:R | ff_lib_7:R_0603_ff | ~
 |  | R72 | 1k 1% | Device:R | ff_lib_7:R_0603_ff | ~
 |  | R73 | 10k 1% | Device:R | ff_lib_7:R_0603_ff | ~
 |  | R74 | 10k 1% | Device:R | ff_lib_7:R_0603_ff | ~
 |  | R75 | 47R | Device:R | Resistor_SMD:R_0805_2012Metric | ~
 |  | R76 | DNP | Device:R | Resistor_SMD:R_0805_2012Metric | ~
 |  | R77 | 10R | Device:R | ff_lib_7:R_0603_ff | ~
 |  | R78 | 10R | Device:R | ff_lib_7:R_0603_ff | ~
 |  | R79 | 0R02 0,5% 1W 50ppm | Device:R | Resistor_SMD:R_2512_6332Metric | ~ | LVK24R020DER
 |  | R80 | 24,9kk 1% | Device:R | ff_lib_7:R_0603_ff | ~
 |  | R81 | 24,9kk 1% | Device:R | ff_lib_7:R_0603_ff | ~
 |  | R82 | 10k 1% | Device:R | ff_lib_7:R_0603_ff | ~
 |  | R83 | 10k 1% | Device:R | ff_lib_7:R_0603_ff | ~
 |  | R84 | 100R | Device:R | Resistor_SMD:R_0805_2012Metric | ~
 |  | RN1 | CAT16-220J4LF | Device:R_Pack04 | Resistor_SMD:R_Array_Concave_4x0603 | ~
 |  | RN2 | CAT16-220J4LF | Device:R_Pack04 | Resistor_SMD:R_Array_Concave_4x0603 | ~
 |  | RN3 | CAT16-102J4LF | Device:R_Pack04 | Resistor_SMD:R_Array_Concave_4x0603 | ~
 |  | RN4 | CAT16-102J4LF | Device:R_Pack04 | Resistor_SMD:R_Array_Concave_4x0603 | ~
 |  | RSR2 | TestPoint | Connector:TestPoint | TestPoint:TestPoint_THTPad_1.5x1.5mm_Drill0.7mm | ~
 |  | RST2 | TestPoint | Connector:TestPoint | TestPoint:TestPoint_THTPad_1.5x1.5mm_Drill0.7mm | ~
 |  | SD1 | DM3AT-SF-PEJM5 | c3Av2_A-rescue:Micro_SD_Card_Det-Connector | Connector_Card:microSD_HC_Hirose_DM3AT-SF-PEJM5 | https://www.hirose.com/product/document?clcode=CL0609-0033-6-00&productname=DM3AT-SF-PEJ2M5&series=DM3&documenttype=Catalog&lang=en&documentid=D49662_en
 |  | T1 | BSC028N06NSATMA1 | Transistor_FET:BSC028N06LS3 | Package_TO_SOT_SMD:TDSON-8-1 | http://www.infineon.com/dgdl/Infineon-BSC028N06LS3-DS-v02_02-en.pdf?fileId=db3a30431ddc9372011ebafa4c607f8c
 |  | T2 | BSC028N06NSATMA1 | Transistor_FET:BSC028N06LS3 | Package_TO_SOT_SMD:TDSON-8-1 | http://www.infineon.com/dgdl/Infineon-BSC028N06LS3-DS-v02_02-en.pdf?fileId=db3a30431ddc9372011ebafa4c607f8c
 |  | T3 | BSC028N06NSATMA1 | Transistor_FET:BSC028N06LS3 | Package_TO_SOT_SMD:TDSON-8-1 | http://www.infineon.com/dgdl/Infineon-BSC028N06LS3-DS-v02_02-en.pdf?fileId=db3a30431ddc9372011ebafa4c607f8c
 |  | T4 | BSC028N06NSATMA1 | Transistor_FET:BSC028N06LS3 | Package_TO_SOT_SMD:TDSON-8-1 | http://www.infineon.com/dgdl/Infineon-BSC028N06LS3-DS-v02_02-en.pdf?fileId=db3a30431ddc9372011ebafa4c607f8c
 |  | T5 | BSC028N06NSATMA1 | Transistor_FET:BSC028N06LS3 | Package_TO_SOT_SMD:TDSON-8-1 | http://www.infineon.com/dgdl/Infineon-BSC028N06LS3-DS-v02_02-en.pdf?fileId=db3a30431ddc9372011ebafa4c607f8c
 |  | T6 | BSC028N06NSATMA1 | Transistor_FET:BSC028N06LS3 | Package_TO_SOT_SMD:TDSON-8-1 | http://www.infineon.com/dgdl/Infineon-BSC028N06LS3-DS-v02_02-en.pdf?fileId=db3a30431ddc9372011ebafa4c607f8c
 |  | T7 | BSC028N06NSATMA1 | Transistor_FET:BSC028N06LS3 | Package_TO_SOT_SMD:TDSON-8-1 | http://www.infineon.com/dgdl/Infineon-BSC028N06LS3-DS-v02_02-en.pdf?fileId=db3a30431ddc9372011ebafa4c607f8c
 |  | T8 | BSC028N06NSATMA1 | Transistor_FET:BSC028N06LS3 | Package_TO_SOT_SMD:TDSON-8-1 | http://www.infineon.com/dgdl/Infineon-BSC028N06LS3-DS-v02_02-en.pdf?fileId=db3a30431ddc9372011ebafa4c607f8c
 |  | T9 | BSC028N06NSATMA1 | Transistor_FET:BSC028N06LS3 | Package_TO_SOT_SMD:TDSON-8-1 | http://www.infineon.com/dgdl/Infineon-BSC028N06LS3-DS-v02_02-en.pdf?fileId=db3a30431ddc9372011ebafa4c607f8c
 |  | T10 | BSC028N06NSATMA1 | Transistor_FET:BSC028N06LS3 | Package_TO_SOT_SMD:TDSON-8-1 | http://www.infineon.com/dgdl/Infineon-BSC028N06LS3-DS-v02_02-en.pdf?fileId=db3a30431ddc9372011ebafa4c607f8c
 |  | T11 | BSC028N06NSATMA1 | Transistor_FET:BSC028N06LS3 | Package_TO_SOT_SMD:TDSON-8-1 | http://www.infineon.com/dgdl/Infineon-BSC028N06LS3-DS-v02_02-en.pdf?fileId=db3a30431ddc9372011ebafa4c607f8c
 |  | T12 | BSC028N06NSATMA1 | Transistor_FET:BSC028N06LS3 | Package_TO_SOT_SMD:TDSON-8-1 | http://www.infineon.com/dgdl/Infineon-BSC028N06LS3-DS-v02_02-en.pdf?fileId=db3a30431ddc9372011ebafa4c607f8c
 |  | T14 | DMP3007SFG-7 | Transistor_FET:DMP3013SFV | ff_lib_7:Diodes_PowerDI3333-8 | https://www.diodes.com/assets/Datasheets/DMP3007SFG.pdf | DMP4013LFG-7
 |  | T15 | DMP3007SFG-7 | Transistor_FET:DMP3013SFV | ff_lib_7:Diodes_PowerDI3333-8 | https://www.diodes.com/assets/Datasheets/DMP3007SFG.pdf | DMP4013LFG-7
 |  | U2 | MAX3250CAI+ | ff:MAX3250CAI | Package_SO:SSOP-28_5.3x10.2mm_P0.65mm | https://datasheets.maximintegrated.com/en/ds/MAX3250.pdf | MAX3250EAI+
 |  | U3 | ADR443BRZ | Reference_Voltage:ADR423ARMZ | Package_SO:SOIC-8_3.9x4.9mm_P1.27mm | https://www.analog.com/media/en/technical-documentation/data-sheets/ADR440_441_443_444_445.pdf
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

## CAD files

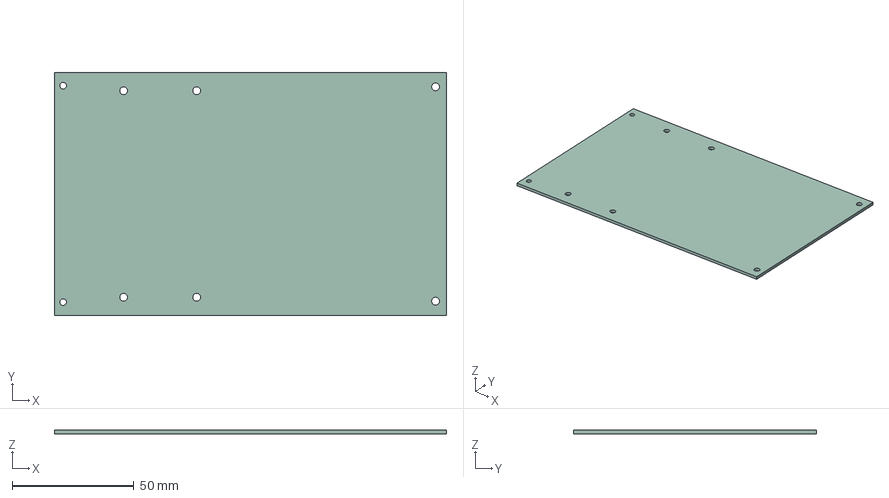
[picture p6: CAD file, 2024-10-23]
kicad/model/artiq_base.step
161.0 x 100.0 x 1.58 mm

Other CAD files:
kicad/model/artiq_base.FCStd

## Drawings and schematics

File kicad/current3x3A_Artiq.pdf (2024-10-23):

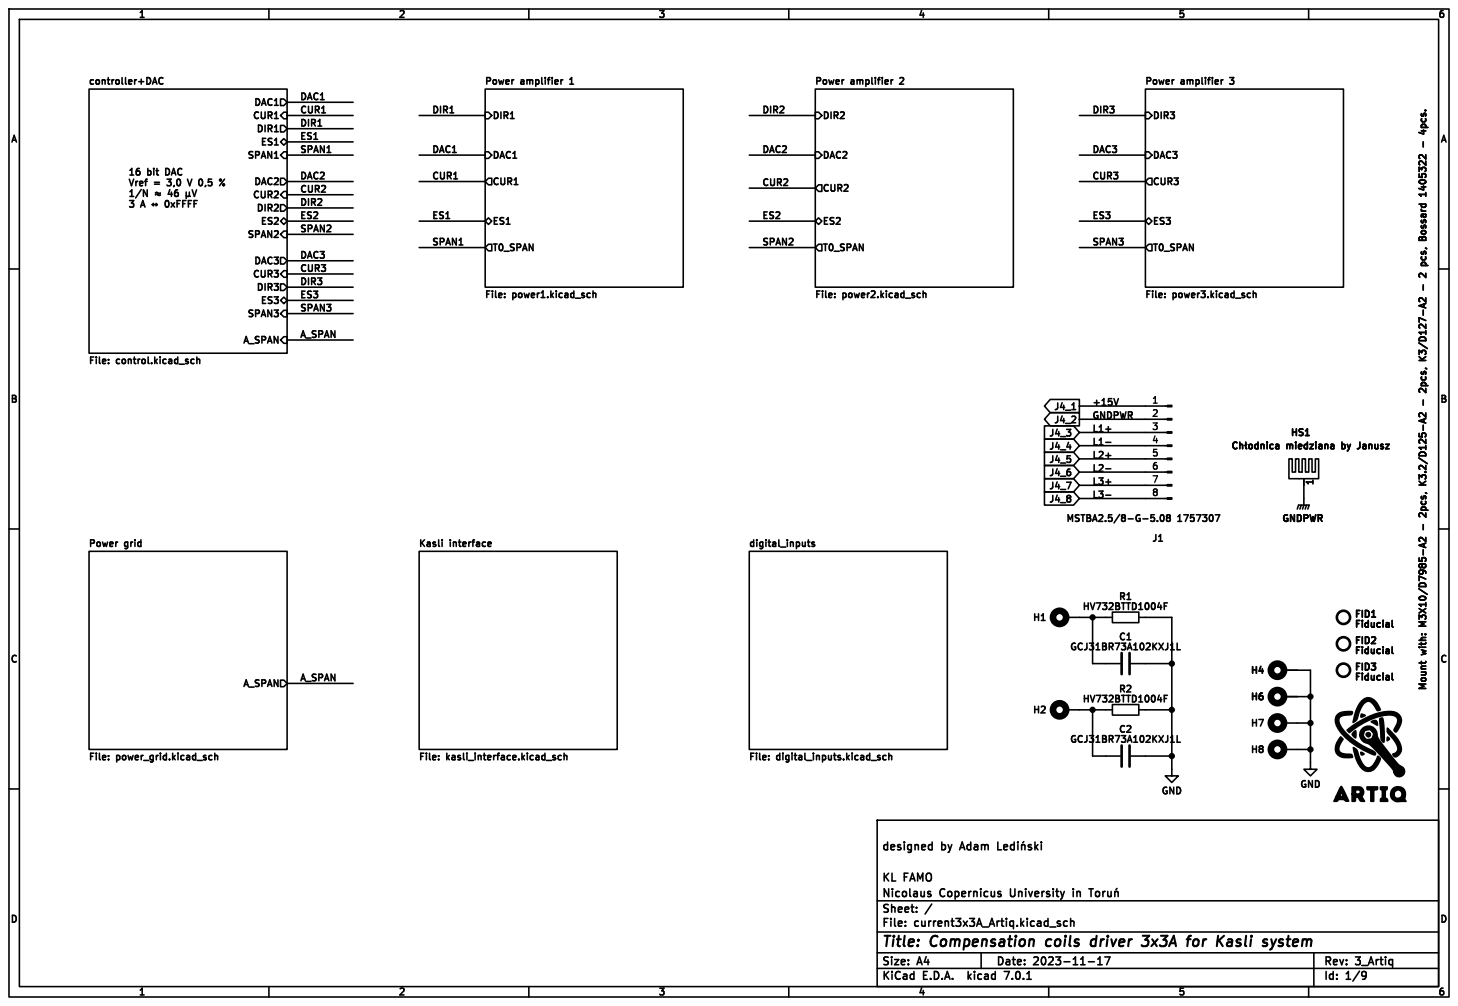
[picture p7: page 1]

digital_inputs File: digital_inputs.kicad_sch Kasli interface File: kasli_interface.kicad_sch A_SPAN

Id: 1/9 Title: Compensation coils driver 3x3A for Kasli system

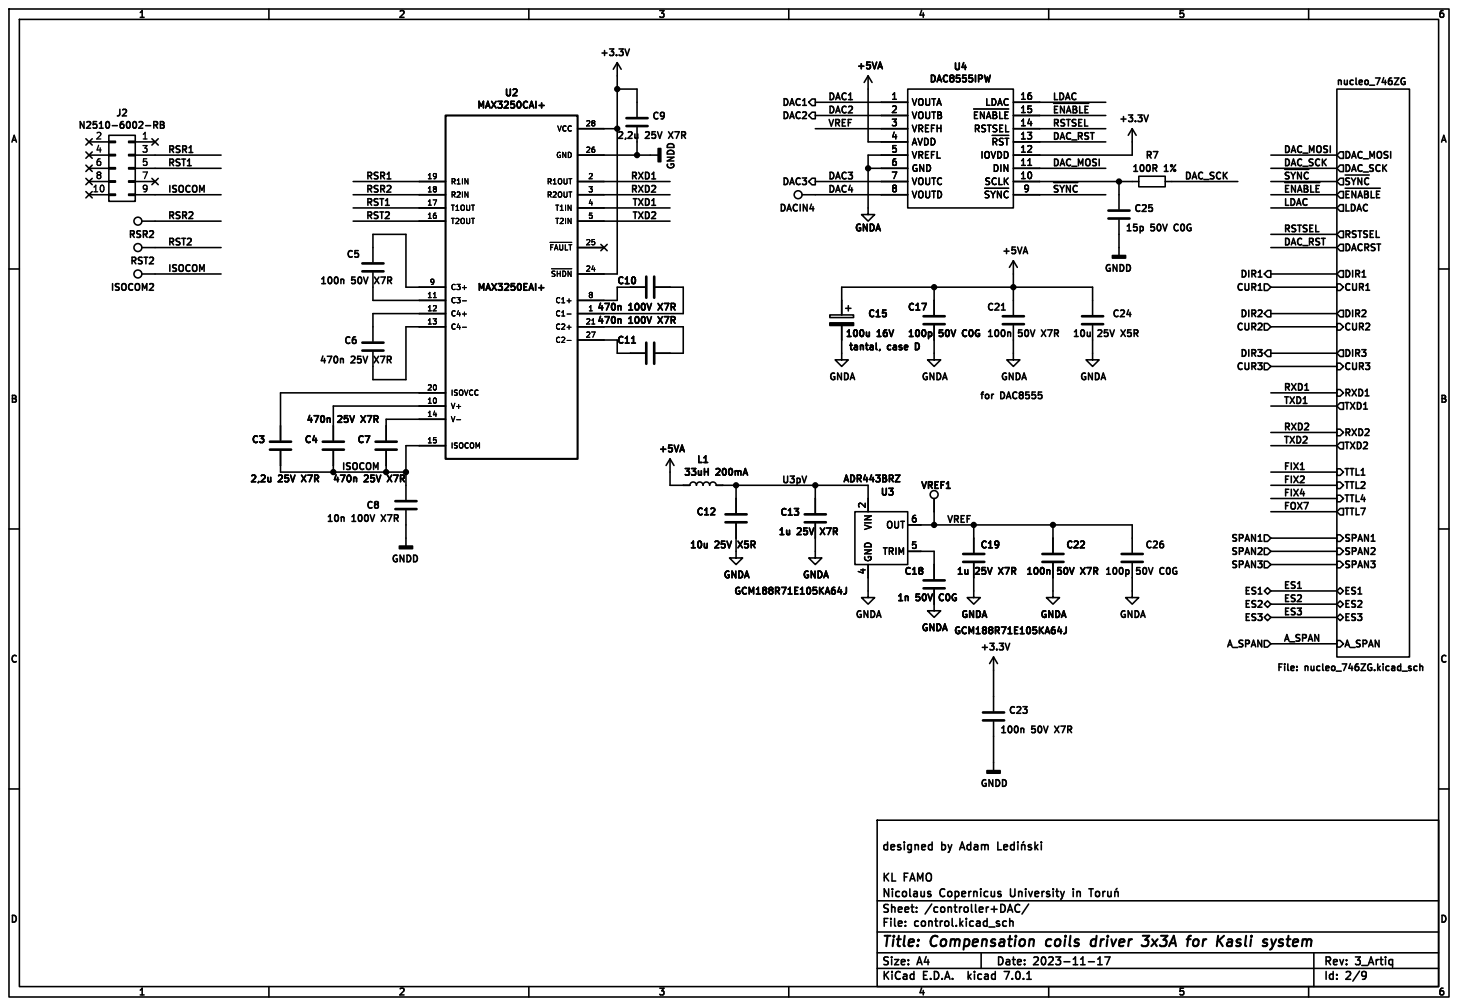
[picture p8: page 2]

Id: 2/9 Title: Compensation coils driver 3x3A for Kasli system

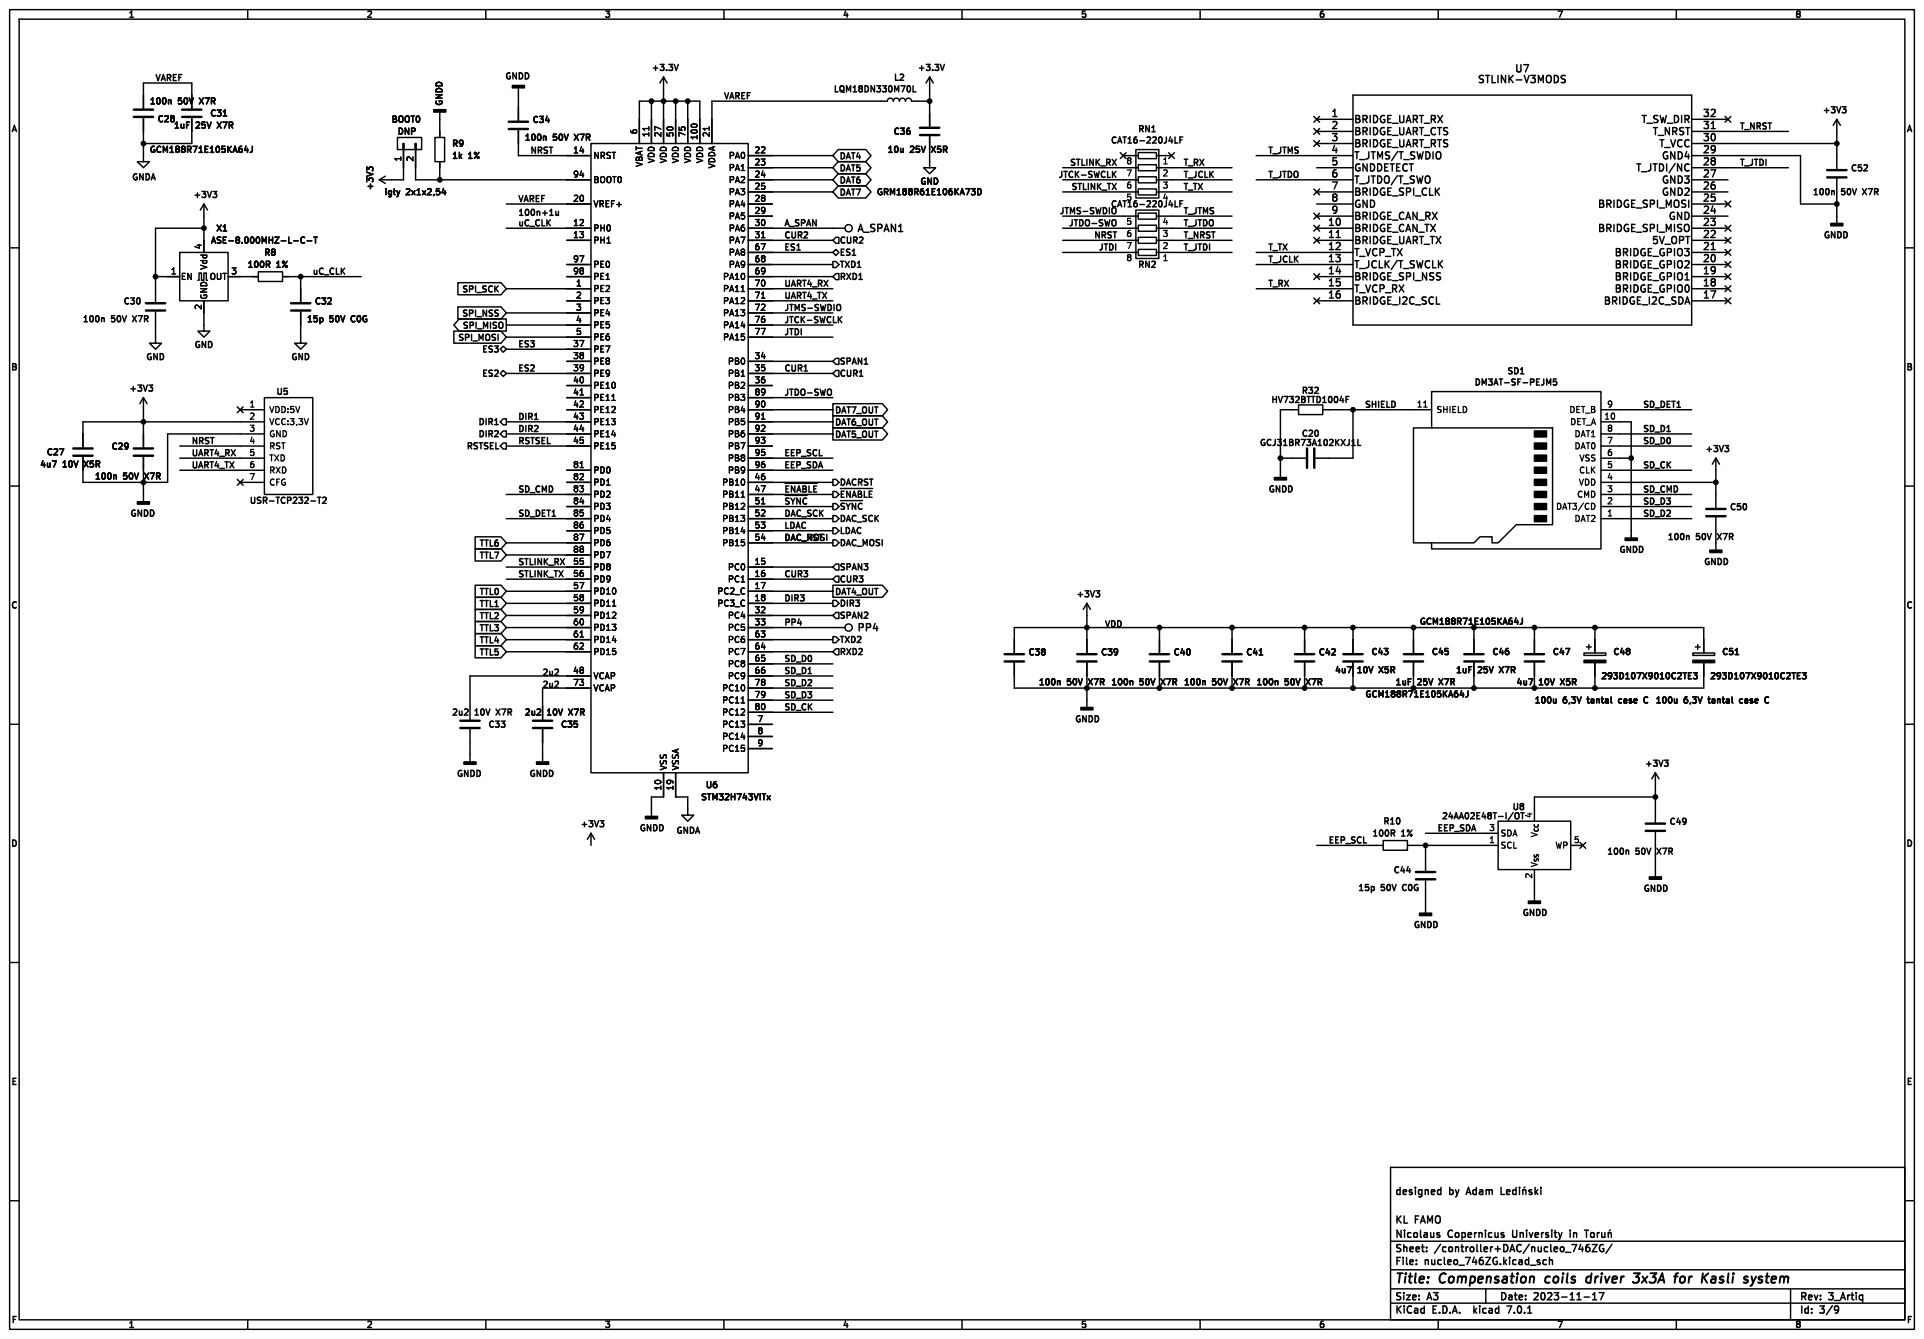
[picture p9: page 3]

Id: 3/9 Title: Compensation coils driver 3x3A for Kasli system

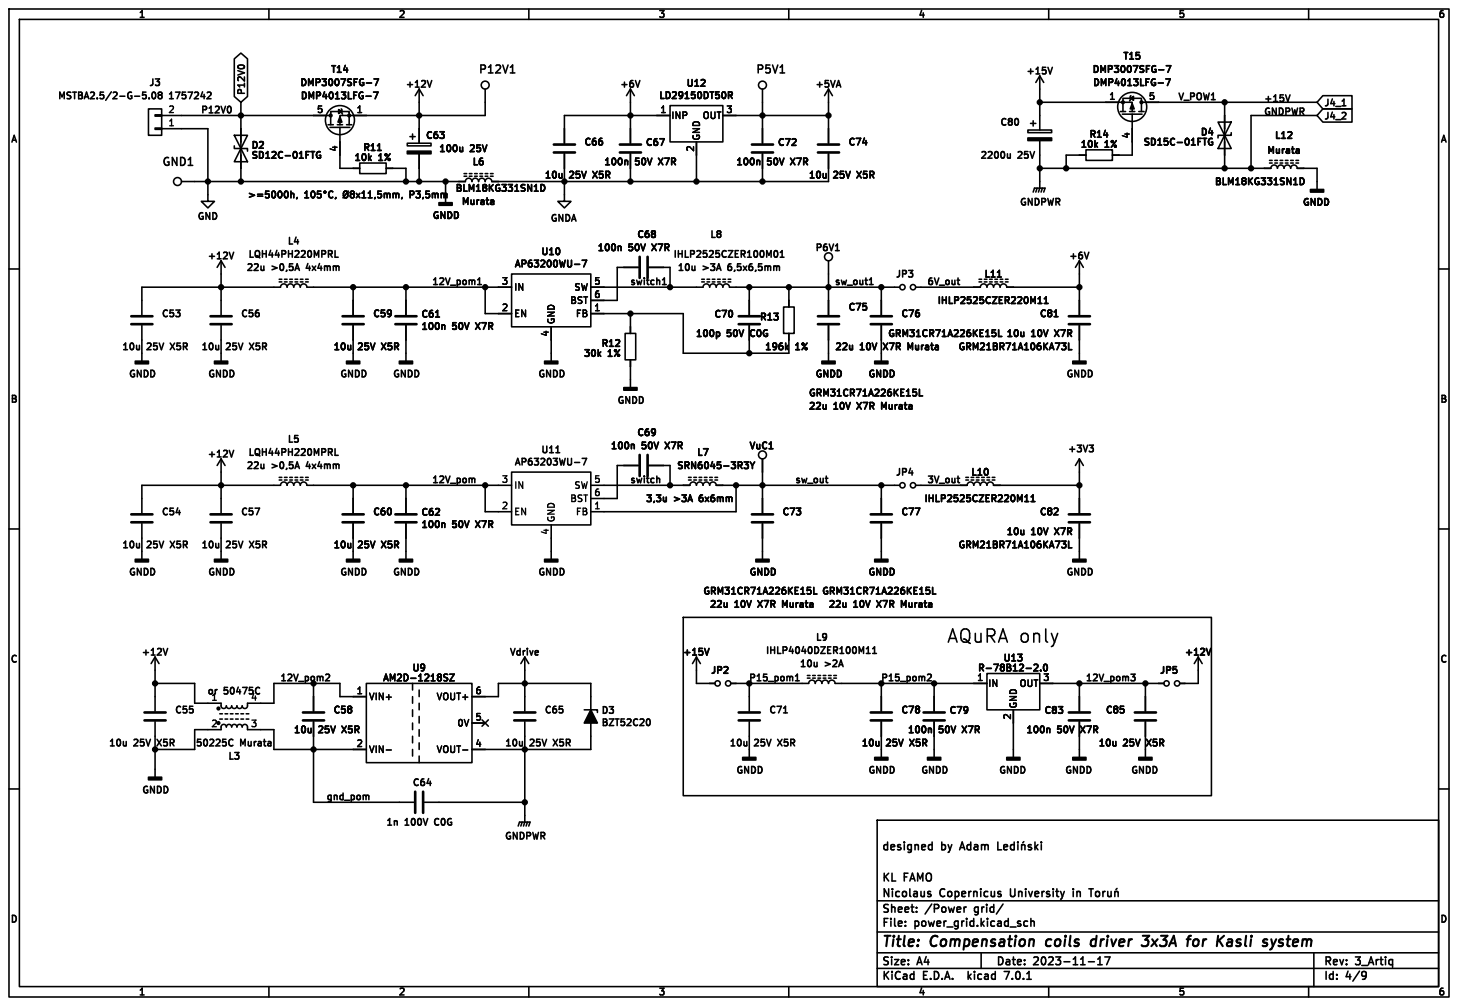
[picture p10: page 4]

Id: 4/9 Title: Compensation coils driver 3x3A for Kasli system

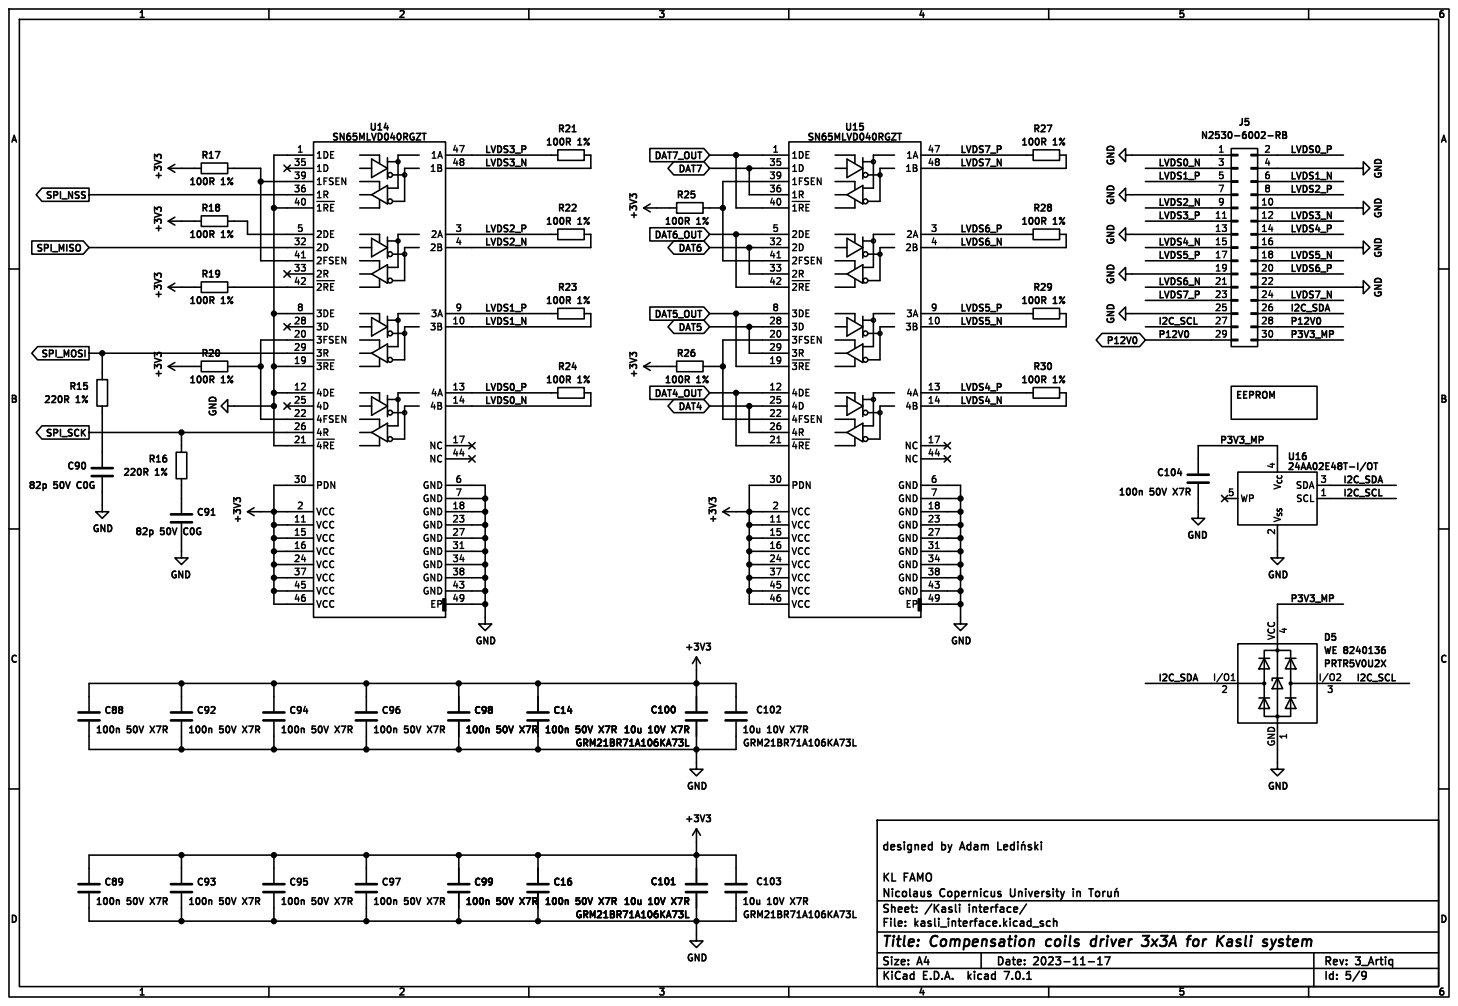
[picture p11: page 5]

J5 N2530-6002-RB GND GND GND

Id: 5/9 Title: Compensation coils driver 3x3A for Kasli system

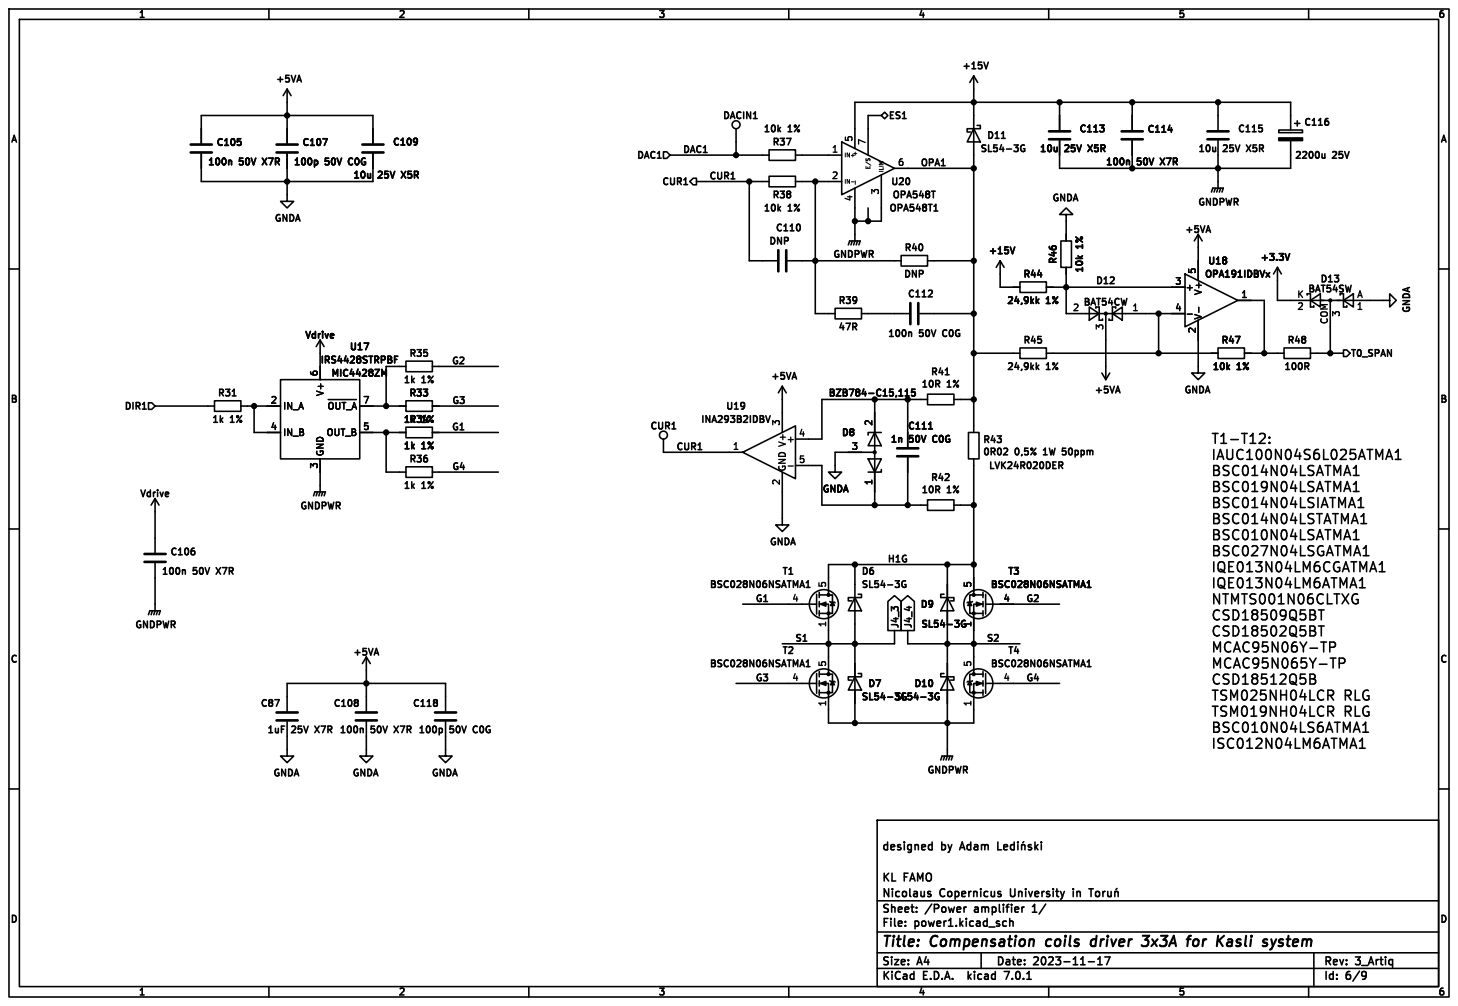
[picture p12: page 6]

Id: 6/9 Title: Compensation coils driver 3x3A for Kasli system

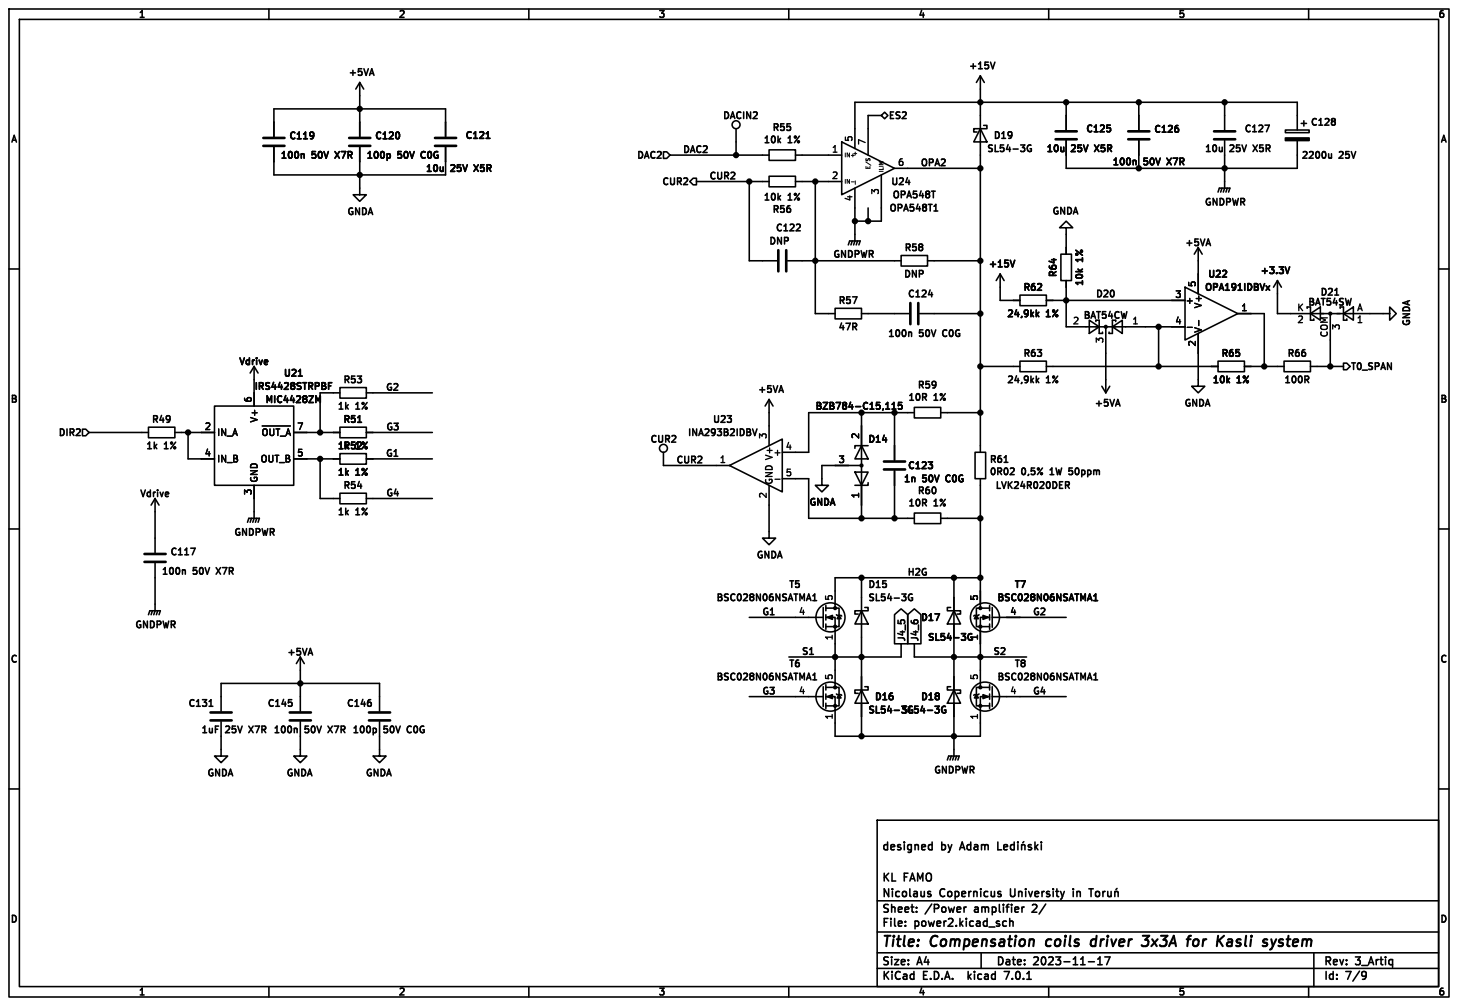
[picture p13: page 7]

Id: 7/9 Title: Compensation coils driver 3x3A for Kasli system

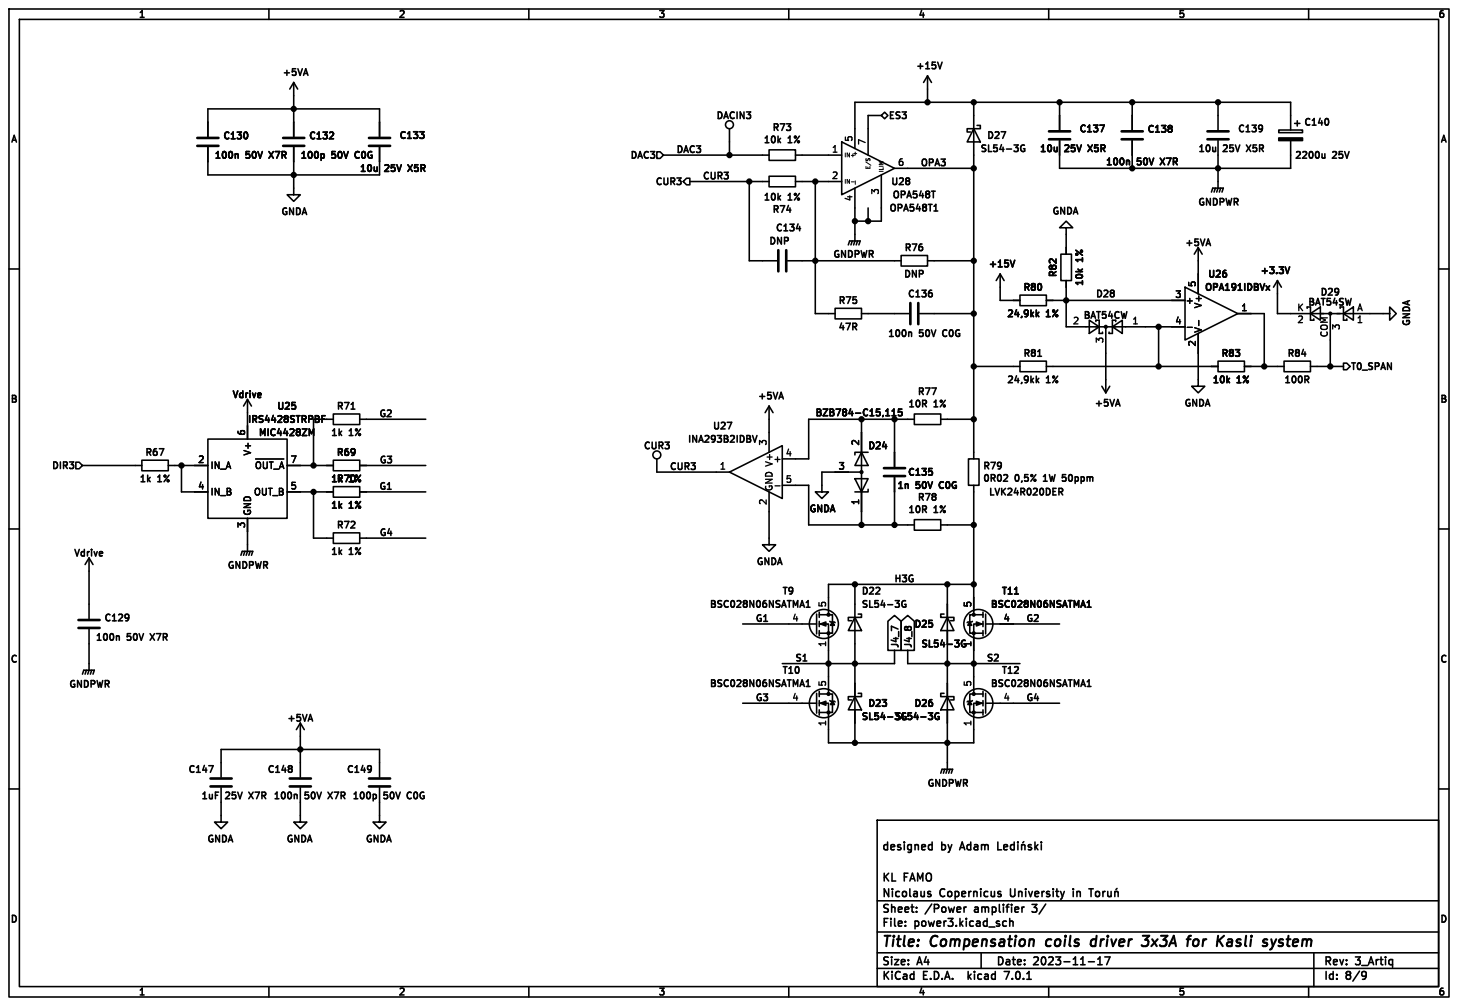
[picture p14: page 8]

Id: 8/9 Title: Compensation coils driver 3x3A for Kasli system

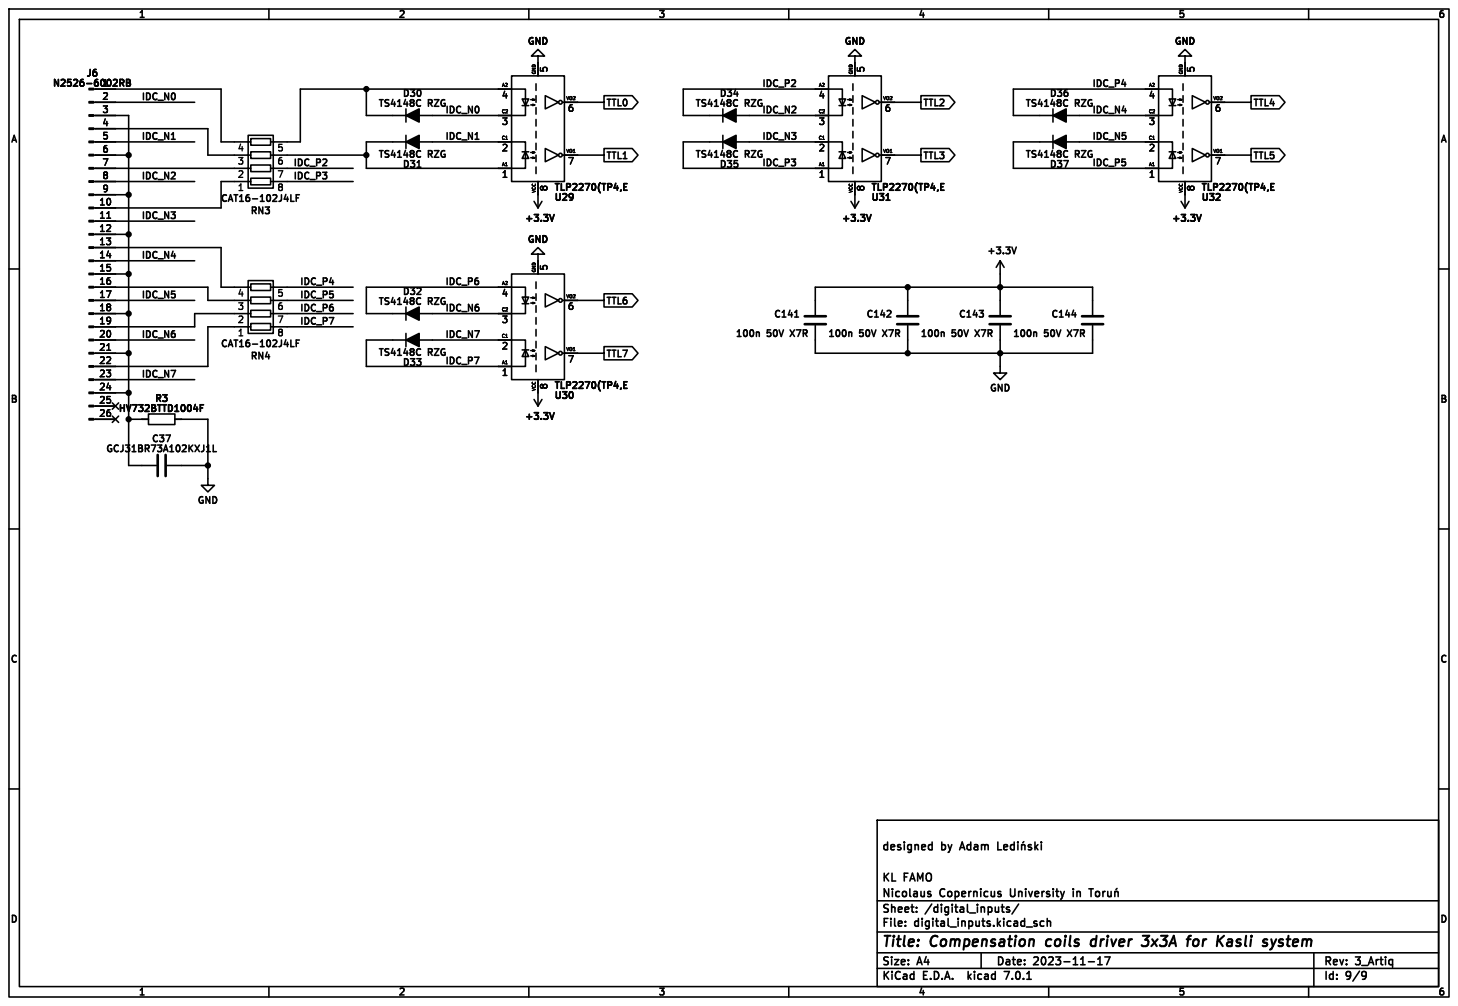
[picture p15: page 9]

Id: 9/9 Title: Compensation coils driver 3x3A for Kasli system

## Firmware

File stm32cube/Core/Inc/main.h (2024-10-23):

/* USER CODE BEGIN Header */
/**
  ******************************************************************************
  * @file           : main.h
  * @brief          : Header for main.c file.
  *                   This file contains the common defines of the application.
  ******************************************************************************
  * @attention
  *
  * Copyright (c) 2024 STMicroelectronics.
  * All rights reserved.
  *
  * This software is licensed under terms that can be found in the LICENSE file
  * in the root directory of this software component.
  * If no LICENSE file comes with this software, it is provided AS-IS.
  *
  ******************************************************************************
  */
/* USER CODE END Header */

/* Define to prevent recursive inclusion -------------------------------------*/
#ifndef __MAIN_H
#define __MAIN_H

#ifdef __cplusplus
extern "C" {
#endif

/* Includes ------------------------------------------------------------------*/
#include "stm32h7xx_hal.h"

/* Private includes ----------------------------------------------------------*/
/* USER CODE BEGIN Includes */

/* USER CODE END Includes */

/* Exported types ------------------------------------------------------------*/
/* USER CODE BEGIN ET */

/* USER CODE END ET */

/* Exported constants --------------------------------------------------------*/
/* USER CODE BEGIN EC */

/* USER CODE END EC */

/* Exported macro ------------------------------------------------------------*/
/* USER CODE BEGIN EM */

/* USER CODE END EM */

/* Exported functions prototypes ---------------------------------------------*/
void Error_Handler(void);

/* USER CODE BEGIN EFP */

/* USER CODE END EFP */

/* Private defines -----------------------------------------------------------*/
#define CUR3_Pin GPIO_PIN_0
#define CUR3_GPIO_Port GPIOC
#define SPAN3_Pin GPIO_PIN_1
#define SPAN3_GPIO_Port GPIOC
#define DAT4_OUT_Pin GPIO_PIN_2
#define DAT4_OUT_GPIO_Port GPIOC
#define DIR3_Pin GPIO_PIN_3
#define DIR3_GPIO_Port GPIOC
#define DAT4_Pin GPIO_PIN_0
#define DAT4_GPIO_Port GPIOA
#define DAT5_Pin GPIO_PIN_1
#define DAT5_GPIO_Port GPIOA
#define DAT6_Pin GPIO_PIN_2
#define DAT6_GPIO_Port GPIOA
#define DAT7_Pin GPIO_PIN_3
#define DAT7_GPIO_Port GPIOA
#define A_SPAN_Pin GPIO_PIN_6
#define A_SPAN_GPIO_Port GPIOA
#define SPAN2_Pin GPIO_PIN_7
#define SPAN2_GPIO_Port GPIOA
#define CUR2_Pin GPIO_PIN_4
#define CUR2_GPIO_Port GPIOC
#define PP4_Pin GPIO_PIN_5
#define PP4_GPIO_Port GPIOC
#define SPAN1_Pin GPIO_PIN_0
#define SPAN1_GPIO_Port GPIOB
#define CUR1_Pin GPIO_PIN_1
#define CUR1_GPIO_Port GPIOB
#define ES3_Pin GPIO_PIN_7
#define ES3_GPIO_Port GPIOE
#define ES3_EXTI_IRQn EXTI9_5_IRQn
#define ES2_Pin GPIO_PIN_9
#define ES2_GPIO_Port GPIOE
#define ES2_EXTI_IRQn EXTI9_5_IRQn
#define DIR1_Pin GPIO_PIN_13
#define DIR1_GPIO_Port GPIOE
#define DIR2_Pin GPIO_PIN_14
#define DIR2_GPIO_Port GPIOE
#define RSTSEL_Pin GPIO_PIN_15
#define RSTSEL_GPIO_Port GPIOE
#define DACRST_Pin GPIO_PIN_10
#define DACRST_GPIO_Port GPIOB
#define ENABLE_Pin GPIO_PIN_11
#define ENABLE_GPIO_Port GPIOB
#define DAC_SYNC_Pin GPIO_PIN_12
#define DAC_SYNC_GPIO_Port GPIOB
#define DAC_SCK_Pin GPIO_PIN_13
#define DAC_SCK_GPIO_Port GPIOB
#define LDAC_Pin GPIO_PIN_14
#define LDAC_GPIO_Port GPIOB
#define DAC_MOSI_Pin GPIO_PIN_15
#define DAC_MOSI_GPIO_Port GPIOB
#define STLINK_RX_Pin GPIO_PIN_8
#define STLINK_RX_GPIO_Port GPIOD
#define STLINK_TX_Pin GPIO_PIN_9
#define STLINK_TX_GPIO_Port GPIOD
#define TTL0_Pin GPIO_PIN_10
#define TTL0_GPIO_Port GPIOD
#define TTL0_EXTI_IRQn EXTI15_10_IRQn
#define TTL1_Pin GPIO_PIN_11
#define TTL1_GPIO_Port GPIOD
#define TTL1_EXTI_IRQn EXTI15_10_IRQn
#define TTL2_Pin GPIO_PIN_12
#define TTL2_GPIO_Port GPIOD
#define TTL2_EXTI_IRQn EXTI15_10_IRQn
#define TTL3_Pin GPIO_PIN_13
#define TTL3_GPIO_Port GPIOD
#define TTL3_EXTI_IRQn EXTI15_10_IRQn
#define TTL4_Pin GPIO_PIN_14
#define TTL4_GPIO_Port GPIOD
#define TTL4_EXTI_IRQn EXTI15_10_IRQn
#define TTL5_Pin GPIO_PIN_15
#define TTL5_GPIO_Port GPIOD
#define TTL5_EXTI_IRQn EXTI15_10_IRQn
#define TXD2_Pin GPIO_PIN_6
#define TXD2_GPIO_Port GPIOC
#define RXD2_Pin GPIO_PIN_7
#define RXD2_GPIO_Port GPIOC
#define ES1_Pin GPIO_PIN_8
#define ES1_GPIO_Port GPIOA
#define ES1_EXTI_IRQn EXTI9_5_IRQn
#define TXD1_Pin GPIO_PIN_9
#define TXD1_GPIO_Port GPIOA
#define RXD1_Pin GPIO_PIN_10
#define RXD1_GPIO_Port GPIOA
#define SD_DET1_Pin GPIO_PIN_4
#define SD_DET1_GPIO_Port GPIOD
#define TTL6_Pin GPIO_PIN_6
#define TTL6_GPIO_Port GPIOD
#define TTL6_EXTI_IRQn EXTI9_5_IRQn
#define DAT7_OUT_Pin GPIO_PIN_4
#define DAT7_OUT_GPIO_Port GPIOB
#define DAT6_OUT_Pin GPIO_PIN_5
#define DAT6_OUT_GPIO_Port GPIOB
#define DAT5_OUT_Pin GPIO_PIN_6
#define DAT5_OUT_GPIO_Port GPIOB

/* USER CODE BEGIN Private defines */

/* USER CODE END Private defines */

#ifdef __cplusplus
}
#endif

#endif /* __MAIN_H */

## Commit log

2024-08-06 adding kicad project
    [C3x3A_A_nucleo_utilisation.ods, analog7.kicad_sch, artiq_base.FCStd, artiq_base.step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]
2024-08-06 creating stm32 project
2024-08-09 added dac functions, initially tested
    [analog7.kicad_sch, artiq_base.step, c3Av2.kicad_sch, control.kicad_sch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]
2024-09-02 notes, tests with another board
2024-11-02 transition time calibration
2024-11-03 using cmd_string_interpret for setting parameters but no current update yet
2025-02-06 all init currents set to 0A
2025-10-01 bugfix wrong current direction
